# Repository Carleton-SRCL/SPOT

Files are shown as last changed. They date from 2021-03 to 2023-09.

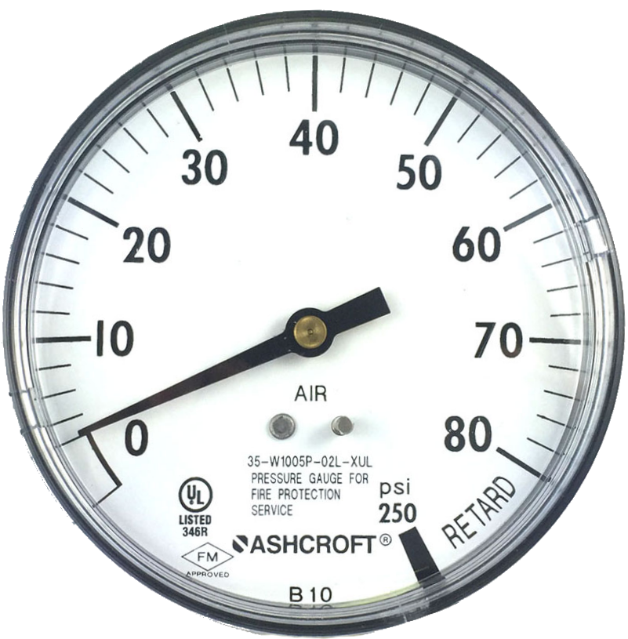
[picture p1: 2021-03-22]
CAD_Files/99 - Textures/guage.png

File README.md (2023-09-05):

# Welcome to SPOT

This testbed is used by researchers to investigate robotics, control and computer vision technologies enabling spacecraft proximity operation tasks, such as inspection maneuvers, rendezvous and docking, robotic capture of a tumbling target, and on-orbit assembly of large structure. SPOT consists of three air-bearing spacecraft platforms operating in close proximity on a granite surface. The use of air bearing on the platforms reduces the friction to a negligible level. Both platforms are actuated by compressed air expelled through small air nozzles, to provide three degree-of-freedom (3DOF) control authority. The motion of all platforms is measured in real-time through LEDs which are tracked by a motion capture system. This provides highly accurate ground truth position and attitude data to evaluate the performance of the new robotics, control, and computer vision technologies.

This repository contains the software developed for SPOT. The software is a mix of Simulink code (making use of existing code that allows us to deploy the Simulink diagrams to a NVIDIA Jetson Xaviers), and custom device driver blocks written in C++ code. It's been designed to be user-friendly, but is a constant work in progress so feedback and bug reports are appreciated. This repository also contains a detailed Wiki on the entire laboratory in an attempt to help guide new users. New users should read this Wiki carefully and watch any related videos before conducting an experiment.

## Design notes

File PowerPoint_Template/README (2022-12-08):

This is a repository to hold Microsoft PowerPoint (.pptx and .potx) template files specifically for use by SRCL students on related work.

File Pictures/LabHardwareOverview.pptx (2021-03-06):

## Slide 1

PhaseSpace Impulse X2E System
H/W: Intel Quad Core
Motion Tracking Camera Array
S/W: Custom Linux Software

Wireless Ethernet (UDP)

Off-Board Development Computer
H/W: Intel Core i7 5775 3.3 GHz
S/W: Window 10, MATLAB 9.8, Simulink 10.1
MATLAB/Simulink Support Package for Raspberry Pi 20.1.0

Wireless Ethernet (UDP)

Air Bearings

On-Board Control Computer
H/W: Raspberry Pi 3 Model B
S/W: Raspbian Linux (10)

Digital Outputs

Analog Outputs

On-Board Machine Learning Computer
H/W: NVIDIA Jetson TX2 Series
S/W: Linux Driver Package (L4T)

On-Board Control Computer
H/W: Raspberry Pi 3 Model B
S/W: Raspbian Linux (10)

Digital Outputs

Analog Outputs

Inertial Measurement Unit
H/W: Yost Labs 3-Space
S/W: Driver 1.1.7

Thrusters

Reaction Wheel

Thrusters

Air Bearings

Robotic Manipulator
H/W: Electromagnetic Dock

Reaction Wheel

Inertial Measurement Unit
H/W: Yost Labs 3-Space
S/W: Driver 1.1.7

Target Spacecraft

Serial (RS232)

On-board Vision System
H/W: ZED 2 Stereo Camera
S/W: OpenCL

Ethernet Hub

Robotic Manipulator
H/W: Dynamixel MX-64
Custom Gripper

Chaser Spacecraft

Serial (RS232)

Granite Table
(3.5 m by 2.4 m)

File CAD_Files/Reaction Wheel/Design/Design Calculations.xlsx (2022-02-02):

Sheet: Mass
Mass Budget

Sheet: Dim
 | POP SSS Sizing |  | 2017-02-05
 | gcs2kgms | gcc2kgcm | mu (km^3/s^2) | Re (km) | g (m/s^2) | R_geo (km) | w_geo (rad/s) | psi2Pa
 | 1e-07 | 1000 | 398600.4418 | 6378.136 | 9.81 | 42164.173 | 7.292115082e-05 | 6894.75789
 | rpm2rps | lbf2N | kg2lb | ft2in | in2cm | deg2rad | rad2deg
 | 0.105 | 4.448222 | 2.20462 | 12 | 2.54 | 0.017 | 57.3
Dimension Scale | 10 | 0.1 | Mass Scale | 200 | 0.005 | Time Scale | 10 | 0.1
Platform Mass Margin |  | 4 |  |  |  | Mission Time Margin |  | 2.25
Bus Sizing | Actual | Platform |  | Actual | Platform | Time Rel Qnty | Actual | Platform
CS bus Dimension |  |  | CS bus mass |  |  | Time (s) | 10 | 1
x length (cm) | 236.2 | 23.6 | BOL Mass (kg) | 3085.5 | 15.4 | Min Linear
y length (cm) | 222.7 | 22.3 | MOL Mass (kg) | 2289 | 11.4 | Min Velocity (m/s) | 0.0145 | 0.0145
z length (cm) | 312.4 | 31.2 | EOL Mass (kg) | 1651.8 | 8.3 | Min Accel (m/s^2) | 0.0135 | 0.135
Solar Panel |  |  | Moment Arm |  |  | Min Angular
CS solar panel (single) |  |  | Expressed in RCSCS |  |  | Min Ang Vel (deg/s) | 0.064 | 0.064
x length (cm) | 212.0 | 21.2 | x COM (cm) | 0.0 | 0.0 | Min Ang Accl (deg/s^2) | 0.000322 | 0.0322
y length (cm) | 312.4 | 31.2 | y COM (cm) | 0.0 | 0.0 | Min Ang Vel (rad/s) | 0.001123992038 | 0.001123992038
z length (cm) | 1.0 | 0.1 | z COM (cm) | 107.8 | 10.8 | Req Ang Vel (rad/s) | 0.001118962667 | 0.01118962667
CS solar panel (total) |  |  |  |  |  | Req Error (rad/s) | 5.029370827e-06 | -0.01006563464
x length (cm) | 212.0 | 21.2 |  |  |  | Min Ang Accl (rad/s^2) | 5.619960191e-06 | 0.0005619960191
y length (cm) | 1329.4 | 132.9 | MOI |  |  | Max Linear
z length (cm) | 1.0 | 0.1 | Expressed in RCSBS |  |  | Max Velocity (m/s) | 0.0135 | 0.0135
num panels | 4.3 |  | xx MOI (kgm^2) | 7123.4 | 0.356 | Max Accel (m/s^2) | 0.0145 | 0.145
 |  |  | yy MOI (kgm^2) | 71.4 | 0.004 | Max Angular
 |  |  | zz MOI (kgm^2) | 7205.6 | 0.360 | Req Ang Vel (rad/s) | 3 | 3
 |  |  | xy MOI (kgm^2) | -1.2 | -6e-05 | Req Error (rad/s) | 0.0 | 0.0
 |  |  | xz MOI (kgm^2) | 0.0 | 0.000 | Max Ang Vel (deg/s) | 3.0 | 3.0
 |  |  | yz MOI (kgm^2) | 0.0 | 0.000 | Max Ang Accl (deg/s^2) | 0.015 | 1.5
 |  |  |  |  |  | Max Ang Vel (rad/s) | 0.05 | 0.05
 |  |  |  |  |  | Max Ang Accl (rad/s^2) | 0.0002617993878 | 0.02617993878
Table Space | (m) | (cm) | Platform MOI Requirement | Unit | Platform | Mission Duration | Actual | Platform
x length | 241.3 | 241.3 | CS yy MOI | (kgm^2) | 0.80 | sec | 33750 | 3375
z length | 350.52 | 350.5 | Margin |  | 2 | min | 562.5 | 56.25
precision | (micro in) | 23.6 | CS yy MOI Req | (kgm^2) | 0.40 | hr | 9.375 | 0.9
 | (micron) | 0.6 | SS yy MOI | (kgm^2) | 0.96 | mission phase
 |  |  | Margin |  | 2 | Phase 1 (min) | 50 | 5
 |  |  | SS yy MOI | (kgm^2) | 0.48 | Phase 2 (min) | 50 | 5
 |  |  |  |  |  | Phase 3 (min) | 50 | 5
 |  |  | Example LEO Orbit | Unit | Actual | Phase 4 (min) | 100 | 10
 |  |  | Altitude | (km) | 450 | Phase 5 (min) | 50 | 5
 |  |  | Orbit Radius | (km) | 6828.13649
 |  |  | Orbit Freq | (rad/s) | 0.001118962667
 |  |  |  | (rpm) | 0.011
 |  |  | Orbit Period | (min) | 93.58646018
Thruster Sizing | Unit | Platform | Wheel Sizing | Unit | Platform | Impulse Requirement | Actual | Platform
Inlet Pressure | (psi) | 20 | Wheel Diameter | (in) | 4 | Pulse Time (s) | 1 | 0.1
Diameter | (mm) | 4 | Height | (in) | 2 | Minimum Impulse Bit
Efficiency |  | 0.5 | Wheel Diameter | (cm) | 10.2 | Num Thruster | 2 | 2
 | (in) | 0.16 | Wheel Height | (cm) | 5.1 | Force per Thruster (lbf) | 2.5 | 0.1
Pressure | (lbf) | 0.2 | Shaft 1 Tolerance |  | 0.1 | After Efficiency Force (N) | 22.2993 | 1.114965
 | (N) | 0.9 | Shaft 1 Diameter | (inch) | 0.95 | After Efficiency Force (lbf) | 5.013081631 | 0.3
Exit Area | (in^2) | 0.02 |  | (cm) | 2.4 | Force per Thruster (N) | 11.14965 | 0.5574825
Num Thruster in Dir |  | 2 | Shaft 1 Length | (inch) | 1.5 | Impulse Bit (Ns) | 22.2993 | 0.1
Total Thrust in Dir | (N) | 1.732841659 |  | (cm) | 3.9 | Delta-V (mm/s) | 13.5 | 13.5
Thruster Pulses |  |  | Shaft 2 Diameter ratio |  | 3 | Maximum Impulse Bit
Minimum |  |  | Shaft 2 Diameter | (inch) | 0.5 | After Efficiency Force (N) | 44.73975 | 2.2369875
Thrust Duration | (sec) | 0.1 |  | (cm) | 1.2 | After Efficiency Force (lbf) | 10.05789504 | 0.5028947521
Impulse Bit | (Ns) | 0.2 | Shaft 2 Length | (inch) | 0.5 | Num Thruster | 4 | 2
Maximum |  |  |  | (cm) | 1.2 | Force per Thruster (lbf) | 2.5 | 0.3
Thrust Duration | (sec) | 1.0 | Wheel Area | (cm^2) | 81.07319666 | Force per Thruster (N) | 11.1849375 | 1.11849375
Impulse Bit | (Ns) | 1.7 | Shaft 1 Area | (cm^2) | 4.599605804 | Impulse Bit (Ns) | 44.73975 | 0.2
 |  |  | Shaft 2 Area | (cm^2) | 1.130973355 | Delta-V (mm/s) | 14.5 | 14.5
MW Motor Sizing | Unit | Platform | Wheel Volume | (cm^3) | 411.851839 | Timings
Gear Box Ratio Calculation |  |  | Shaft 1 Volume | (cm^3) | 17.93846264 | Reaction Timing (s) | 20 | 2
Input Motor Rate | (rpm) | 6800 | Shaft 2 Voume | (cm^3) | 1.334548559 | Minimum Impulse Bit
 | (rad/s) | 712.0943348 | Total Wheel Volume | (cm^3) | 392.5788278 | Req Veh Pitch Torque (Nm) | 0.0004815181892 | 0.0005417079629
Output Ang Rate | (rad/s) | 13.43574217 | Wheel Material |  | Stainless Steel | Req Veh Pitch Torque (mNm) | 0.482 | 0.542
 | (deg/s) | 769.8113208 | Wheel Density | (g/cm^3) | 7.955 | Ang Impulse Bit (Nms) | 0.009630363784 | 0.001
Input Torque | (mNm) | 1.61 | % Volume |  | 1 | Vehicle angular acc (rad/s^2) | 0.0001123992038 | 0.001123992038
Output Torque | (mNm) | 25.23484299 | Wheel Mass | (kg) | 3.1 | Vehicle angular acc (deg/s^2) | 0.00644 | 0.0644
Margin |  | 2 |  | (lb) | 6.884950162 | Vehicle velocity (rad/s) | 0.001 | 0.001
Output With Margin | (mNm) | 50.46968598 | Wheel Area Section 1 | (cm^2) | 76.47359085 | Vehicle velocity (deg/s) | 0.064 | 0.064
GB Ratio |  | 53 | Wheel Area Section 2 | (cm^2) | 79.9422233 | Stack angular rate (rad/s) | 1.590560529e-08 | 0.0001655095759
Est. GB Efficiency |  | 0.59 | Wheel Volume Section 1 | (cm^3) | 298.2470043 | Stack angular rate (deg/s) | 9.113240536e-07 | 0.01
Final Motor GB Combination |  |  | Wheel Volume Section 2 | (cm^3) | 94.33182349 | Stack angular rate (rpm) | 1.518873423e-07 | 0.001580500028
Motor+GB Combined Length | (cm) | 5.34 | Mass Section 1 | (kg) | 2.4 | Stach rotation period (min) | 6583827.099 | 632.7
Motor+GB Inertia | (kgm^2) | 1.43e-06 | Mass Section 2 | (kg) | 0.8 | Maximum Impulse Bit
Load Inertia | (kgm^2) | 0.0074 | Wheel Inertia Section 1 | (kgm^2) | 0.0032 | Req Veh Pitch Torque (Nm) | 0.022 | 0.025
Load Inertia/Rotor Inertia Ratio |  | 5157.308392 | Wheel Inertia Section 2 | (kgm^2) | 0.0010 | Req Veh Pitch Torque (mNm) | 22.4 | 25.2
Gear Ratio req. base on Inertia |  | 71.8144024 | Wheel Inertia CORRECTED BY KIRK | (kgm^2) | 0.0074 | Ang Impulse Bit (Nms) | 0.4486194309 | 0.050
Check GB Ratio | (req.>95%) | 0.74 | Spin Rate | (rpm) | 128.3018868 | Vehicle angular acc (rad/s^2) | 0.005 | 0.052
Motor+GB Out Stall Torque | (mNm) | 248.2839844 | Allowed Spin Rate | (rpm) | 128.3018868 | Vehicle angular acc (deg/s^2) | 0.3 | 3
Motor+GB Out Nominal Torque | (mNm) | 149.428828 | delta |  | 0 | Vehicle velocity (rad/s) | 0.052 | 0.052
Output Speed | (rpm) | 128.3018868 |  | (rev/s) | 2.1 | Vehicle velocity (deg/s) | 3.0 | 3.0
Mechanical Time Constant | (s) | 414.2121638 |  | (rad/s) | 13.43574217 | Stack angular rate (rad/s) | 7.409443457e-07 | 0.007710073412
Motor |  |  |  | (deg/s) | 769.8113208 | Stack angular rate (deg/s) | 4.245298386e-05 | 0.44
Reference | Maxon | http://www.maxonmotor.com/medias/sys_master/root/8816806527006/15-257-EN.pdf | Kinetic Energy | (J) | 0.7 | Stack angular rate (rpm) | 7.075497311e-06 | 0.07362577771
Serial | 339260 | Maxon-EC32flat-32mm,brushless,6W,with Hall | Angular Mom | (Nms) | 0.10 | Stach rotation period (min) | 141332.8217 | 13.6
Mass | (kg) | 0.032 | Margin |  | 2.0 | RWA Design Check | Unit | Platform
Kt | (mNm/A) | 13.2 |  |  |  | Desired platform RPM | rpm | 10
Motor Efficiency |  | 0.57 | Stack Dynamics | Actual | Platform | Desired platform Angular Rate | deg/s | 60
MOI | (gcm^2) | 13.9 | CS yy-MOI Percent Increase | 1.0 | 225 |  | rad/s | 1.047197551
 | (kgm^2) | 1.39e-06 | CS yy-MOI (kgm^2) | 71.4 | 0.80 | Required Wheel Angular Momentum | Nms | 1.00939372
Diameter | (cm) | 3.2 | SS yy-MOI Percent Increase | 1.2 | 270 | Required Wheel MOI Multiplication |  | 10.18684734
Length | (cm) | 1.8 | SS yy-MOI (kgm^2) | 85.68 | 0.96 | Max Platform Angular Rate | deg/s | 5.89
Shaft Diameter | (cm) | 0.4 | Stack CG-CG Distance (cm) | 312.4 | 31.2 | Seconds Per Full Rotation | s | 61.12
Shaft Length | (cm) | 1.0 | MOI addition from CS (kgm^2) | 30116.41041 | 1.5 | Rotations Per Minute | rpm | 0.98
Time Constant | (ms) | 80.3 | Stack yy-MOI (kgm^2) | 30273.49041 | 3.3 | Minutes Per Rotation | min | 1.02
Voltage | (V) | 12 | Initial Condition
Max Power | (W) | 6 | CS Initial Ang Vel (rad/s) | 0.001118962667 | 0.01118962667 | RWA Design Check | Unit | Platform
Max Current | (A) | 0.50 | CS Initial Ang Vel (deg/s) | 0.06 | 0.64 | Required Min Torq on Platform | (Nm) | 0.0005417079629
Idle speed | (rpm) | 7970 | CS Initial Rot Period (min) | 93.58646018 | 9.36 | Required Max Torq on Platform | (Nm) | 0.025
Max Motor Torque | (mNm) | 7.98 | CS Ang Mom (kg-m^2/s) | 0.08 | 0.009 | Max Torq by Gearbox Output | (Nm) | 0.149
Check Max Torque Margin |  | 4.94 | SS Initial Ang Vel (rad/s) | 0.001118962667 | 0.01118962667 | Required Max Ang Mom | (Nms) | 0.050
Running Speed | (rpm) | 6800 | SS Ang Mom (kg-m^2/s) | 0.10 | 0.011 | Max Stack Ang Mom | (Nms) | 0.050
 | (rad/s) | 712.0943348 | Total Ang Mom (kg-m^2/s) | 0.18 | 0.02 | Max Ang Mom Store in Wheel | (Nms) | 0.099
Running Torque | (mNm) | 4.80 | Post stack |  |  | Max Input Torque | (mNm) | 1.61
Check Running Torque Margin |  | 2.98 | % increase Dlt-H FFC (kg-m^2/s) | 1.55 | 1.55 | Max Motor Torque Capable | (mNm) | 7.98
Gear Box |  |  | Total Ang Post FFC (Nms) | 0.45 | 0.05 | Max Computed Motor rate | (rpm) | 6800
Reference | Maxon | http://www.maxonmotor.com/medias/sys_master/root/8816808460318/15-295-296-EN.pdf | Post FFC Ang Vel (rad/s) | 1.480519643e-05 | 0.01540590087 | Max GB input speed | (rpm) | 8000
Serial | 143980 | Planetary Gearhead GP22C | Post FFC Ang Vel (deg/s) | 0.001 | 0.883 | Require Gear Ratio |  | 53.0
Gear Ratio |  | 53 | Post FFC Rot Period (min) | 7073.175664 | 6.797379525 | Selected Gear Ratio |  | 52.7
Absolute Reduction |  | 52.734375
Shaft Diameter | (cm) | 0.4 | Manipulator Sizing | Unit | Platform | Manipulator Design | Unit | Platform
 | (inch) | 0.157 | Link Selection |  |  | Joints
Shaft Length | (cm) | 1.17 | Material |  | carbon fiber | Number of joints |  | 3
Diameter | (cm) | 2.2 | Type |  | Tube | Joint types |  | SR,SY,SP,EP,WP,WY,WR
 | (inch) | 0.866 | Density | (g/cm^3) | 1.55 | Number of links |  | 2
Length | (cm) | 3.9 |  | (kg/m^3) | 1550 | Link types |  | SB,WB
 | (inch) | 1.535 | Bending Tensile Strength | (ksi) | 300 | Power
Mass | (kg) | 0.068 |  | (MPa) | 2068.427367 | Maximum Power | (W) | 72.72
 | (lb) | 0.150 | Bending Modulus | (Msi) | 15 | Power Ref | SRCL-SSFP-150601-01-SK-Mission_Phase_Power_Budget-R1.xls
MOI | (gcm^2) | 0.4 |  | (GPa) | 103.4213683 | Bus Voltage | (V) | 12
 | (kgm^2) | 4e-08 | Bending Shear Modulus | (Msi) | 0.6 | WR | (W) | 24.24
Max Axial Load | (N) | 100 |  | (GPa) | 4.1 | WY | (W) | 24.24
Max Force for Press Fits | (N) | 100 | Torsion Tensile Strength | (ksi) | 20 | WP | (W) | 24.24
Number of Stages |  | 3 |  | (MPa) | 137.8951578 | EP | (W) | 24.24
Avg Backlash No Load | (deg) | 1.6 | Torsion Modulus | (Msi) | 2.2 | SP | (W) | 24.24
GB Efficiency |  | 0.59 |  | (GPa) | 15.16846736 | SY | (W) | 24.24
Max Input Speed | (rpm) | 8000 | Torsion Shear Modulus | (Msi) | 4.5 | SR | (W) | 24.24
 |  |  |  | (GPa) | 31.0264105 | WR Running Current | (A) | 2.02
Max Continuous Torque | (mNm) | 1200 | Boom |  |  | WY Running Current | (A) | 2.02
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

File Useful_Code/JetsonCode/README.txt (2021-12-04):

jetsonRepeater.py is run on the Jetson and communicates to: 1) the Pi; 2) any other scripts running on the Jetson
use_deep_guidance_arm.py is an example of another script that is run on the Jetson and interfaces with the Pi via the jetsonRepeater.py
The remaining scripts are used to capture or perform CNN-inference with the Zed camera.

For a Simulink example of communicating with the Pi, see: https://github.com/Kirkados/SPOT/tree/main/Projects/Kirk_Phase3 and look at the Kirk_Phase3.slx diagram

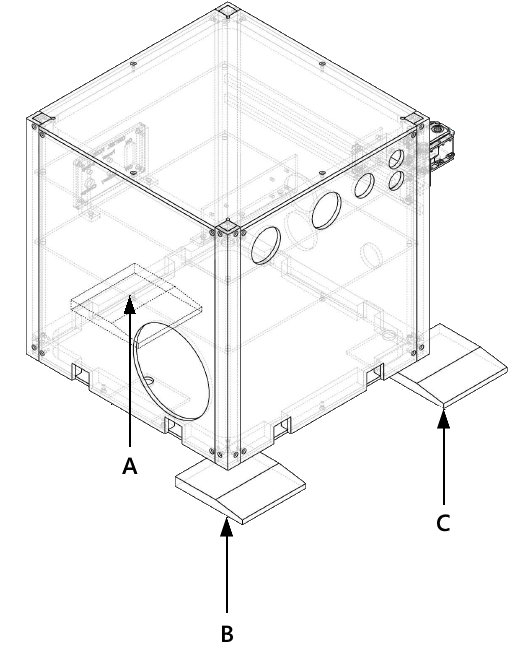
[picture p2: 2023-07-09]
Projects/Capstone_2023_2024/Resources/config_for_com.png

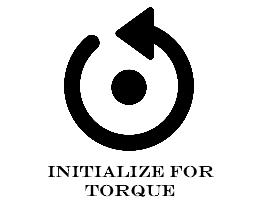
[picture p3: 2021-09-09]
Custom_Library/InitTorque.png

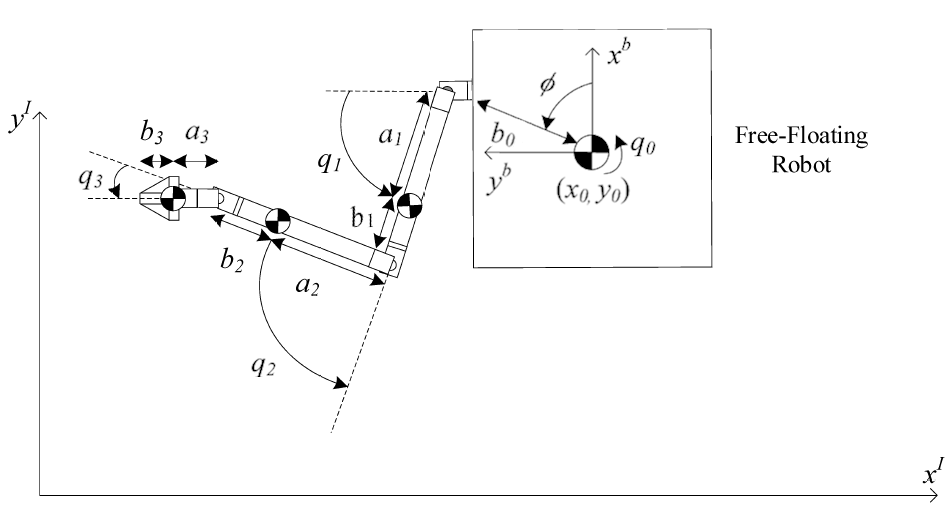
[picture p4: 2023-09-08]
Projects/Capstone_2023_2024/Resources/ArmConfig.png

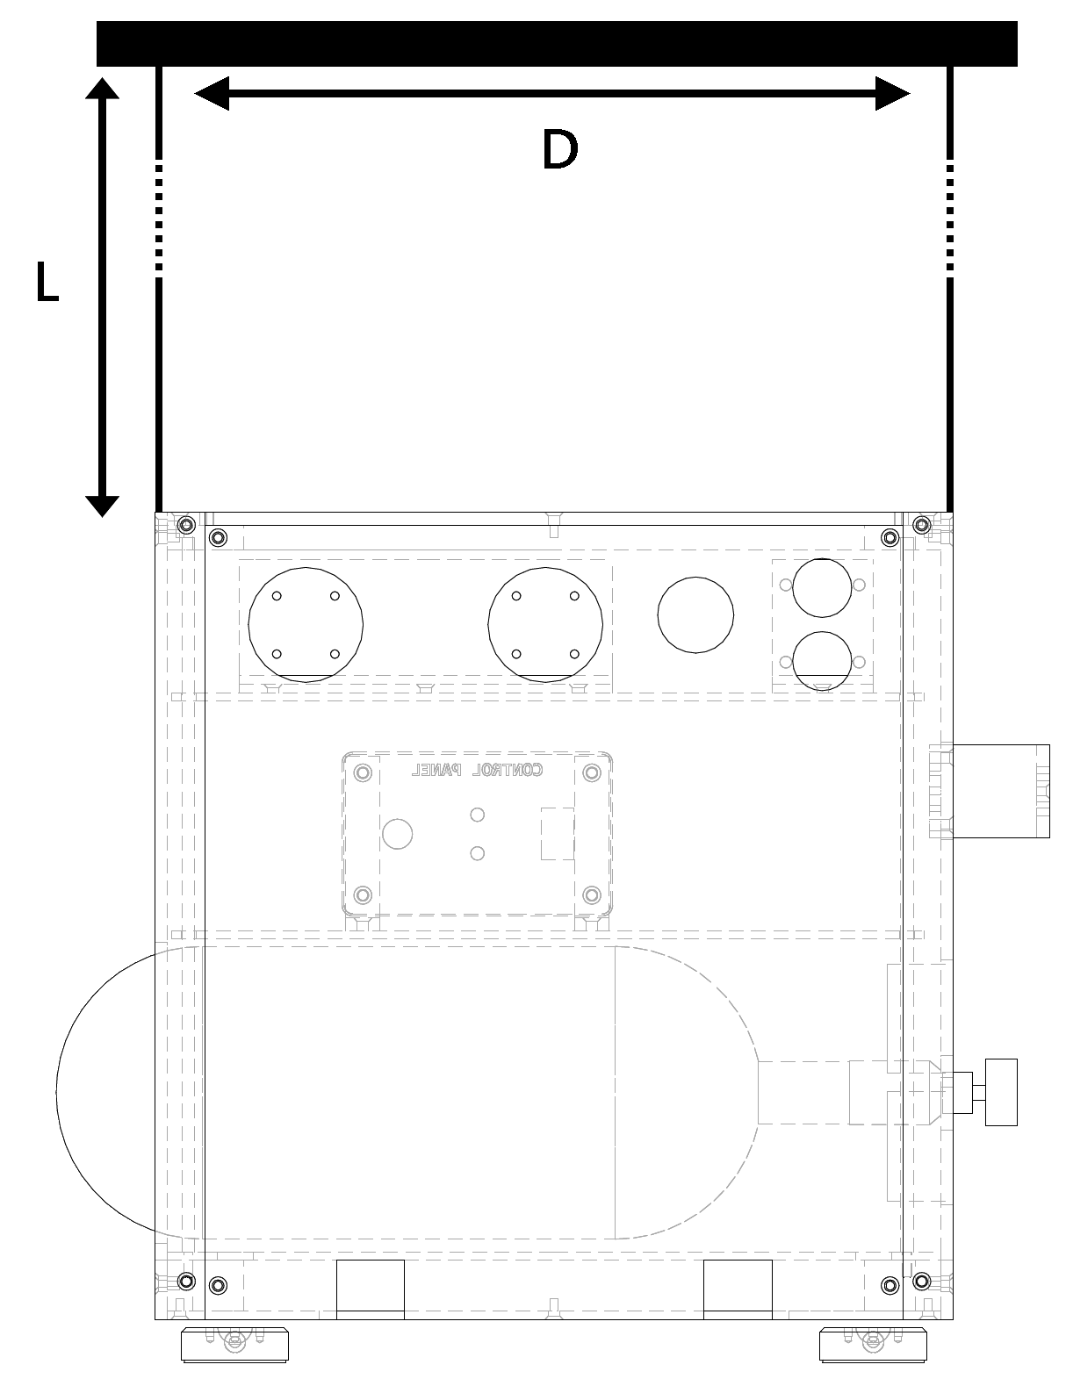
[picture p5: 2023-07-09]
Projects/Capstone_2023_2024/Resources/config_for_inertia.png

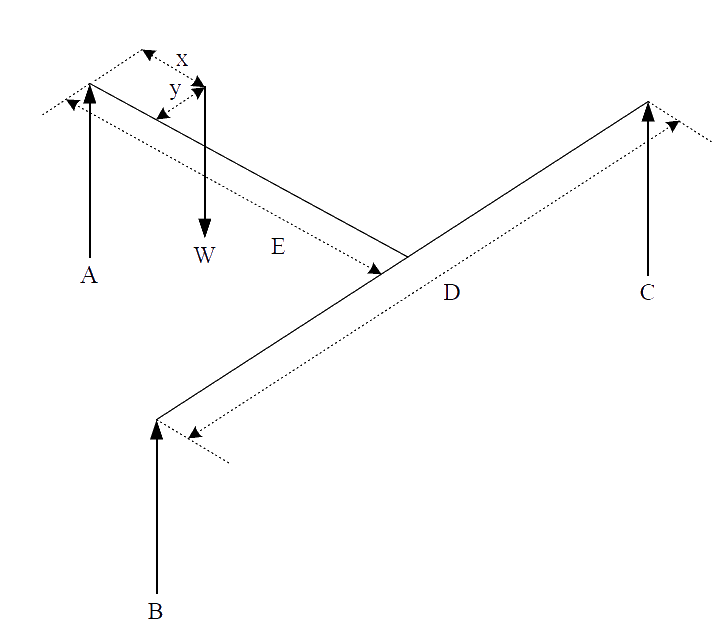
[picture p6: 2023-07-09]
Projects/Capstone_2023_2024/Resources/fbd_for_com.png

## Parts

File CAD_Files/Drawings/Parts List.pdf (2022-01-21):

PART NUMBER | DESCRIPTION | QTY | NOTES
SSFP-001 | Corner Bracket | 8 | QTY of 4 will be used in SSFP-018. Apply
| | | surface finish where applicable
SSFP-002 | Top | 2
SSFP-003 | Rod | 8
SSFP-004 | Bus Deck | 2
SSFP-005 | Protective Plate | 2
SSFP-006 | Deck(AV+SENS) | 4
SSFP-007 | Arm Bracket | 2 | QTY of 2 will be used in SSFP-018. Apply
| | | surface finish where applicable
SSFP-008 | Arm Coupler | 2
SSFP-009 | Control Panel Bracket | 4
SSFP-010 | LIDAR Mount | 2
SSFP-011 | Stereo Mount | 2
SSFP-012 | Control Panel | 2 | Will discuss means of applying text
SSFP-013 | Back Panel | 2
SSFP-014 | Front Panel | 2
SSFP-015 | Left Panel | 2
SSFP-016 | Right Panel | 2
SSFP-017 | Top Panel | 2
SSFP-018 | Weld ASSY | 2

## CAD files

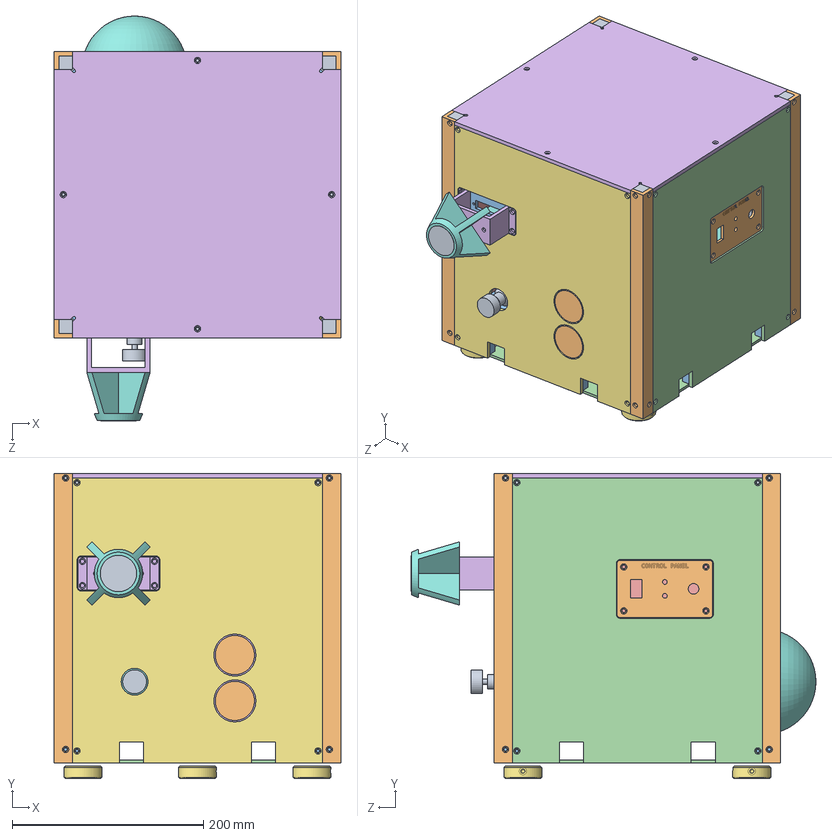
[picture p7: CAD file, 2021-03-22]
CAD_Files/00 - Full_Lab_Assemblies/servicer_no-arm_dock_stereo-ZED.SLDASM
300.0 x 319.3 x 424.0 mm
top
corner-bracket x 4
arm_bracket
panel_back
panel_front
deck_avionics
control_panel_bracket x 2
control_panel
deck_sensor
camera_VIS-mount
camera_Lidar-mount
panel_right
puck x 3
air_tank
air_tank_valve
pressure-gauge x 2
deck_bus
protective_plate
rod x 4
arm_coupler
stereo_camera_ZED-Body
male_cone
disk

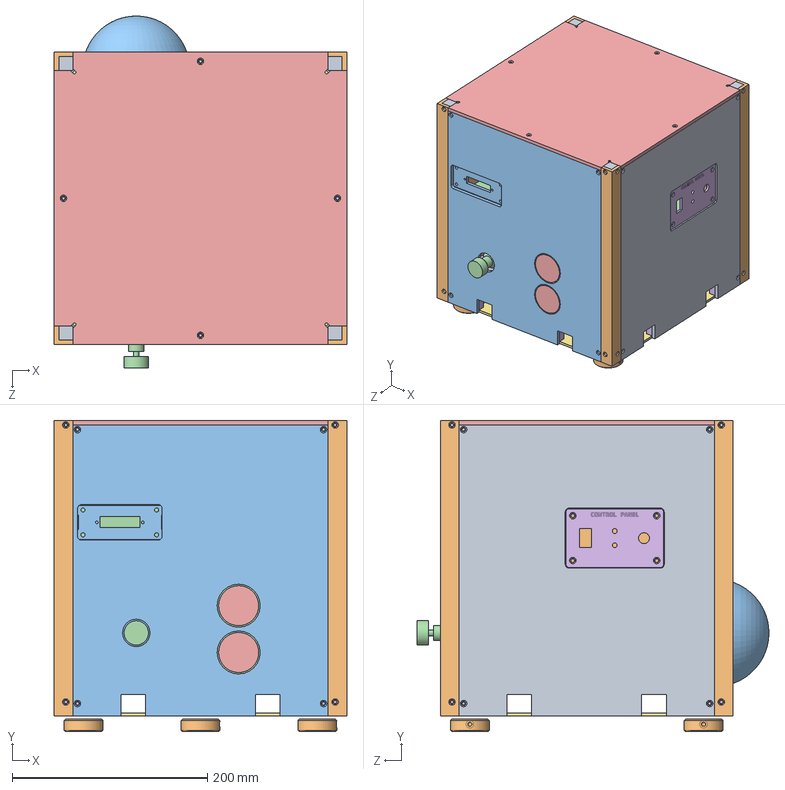
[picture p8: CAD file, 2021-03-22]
CAD_Files/01 - Target/FULLASSY_client.SLDASM
300.0 x 319.4 x 361.0 mm
top
corner-bracket x 4
arm_bracket
deck_avionics
control_panel_bracket x 2
control_panel
deck_sensor
camera_VIS-mount
camera_Lidar-mount
puck x 3
air_tank
air_tank_valve
pressure-gauge x 2
deck_bus
protective_plate
rod x 4
panel_back_black
panel_front_black
panel_left_black
panel_right_black
panel_top_black

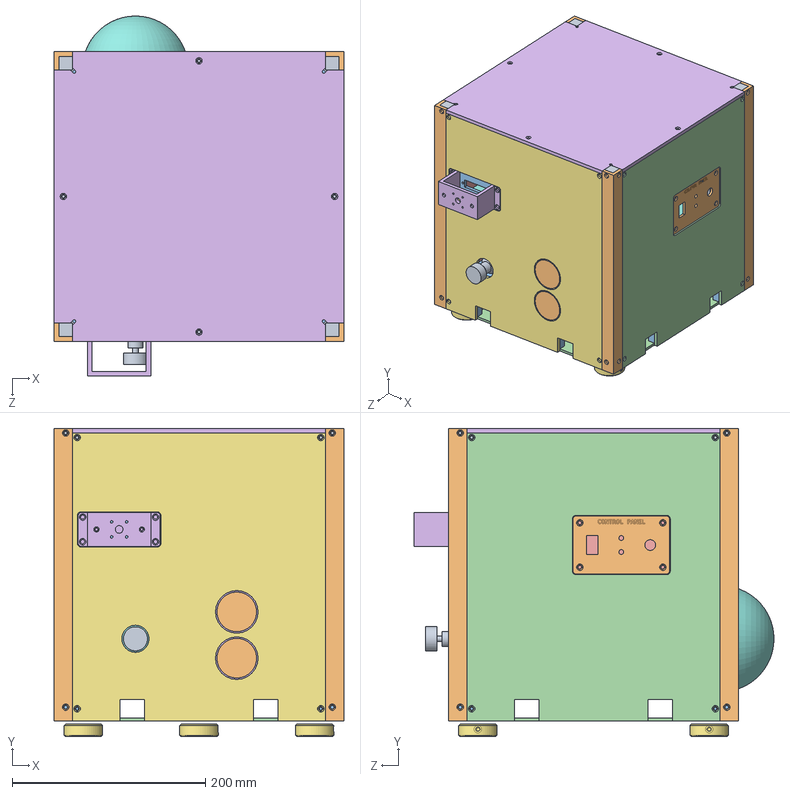
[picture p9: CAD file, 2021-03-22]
CAD_Files/02 - Chaser/FULLASSY_servicer.SLDASM
300.0 x 319.3 x 373.0 mm
top
corner-bracket x 4
arm_bracket
panel_back
panel_front
panel_top
panel_left
deck_avionics
control_panel_bracket x 2
control_panel
deck_sensor
camera_VIS-mount
camera_Lidar-mount
panel_right
puck x 3
air_tank
air_tank_valve
pressure-gauge x 2
deck_bus
protective_plate
rod x 4
arm_coupler

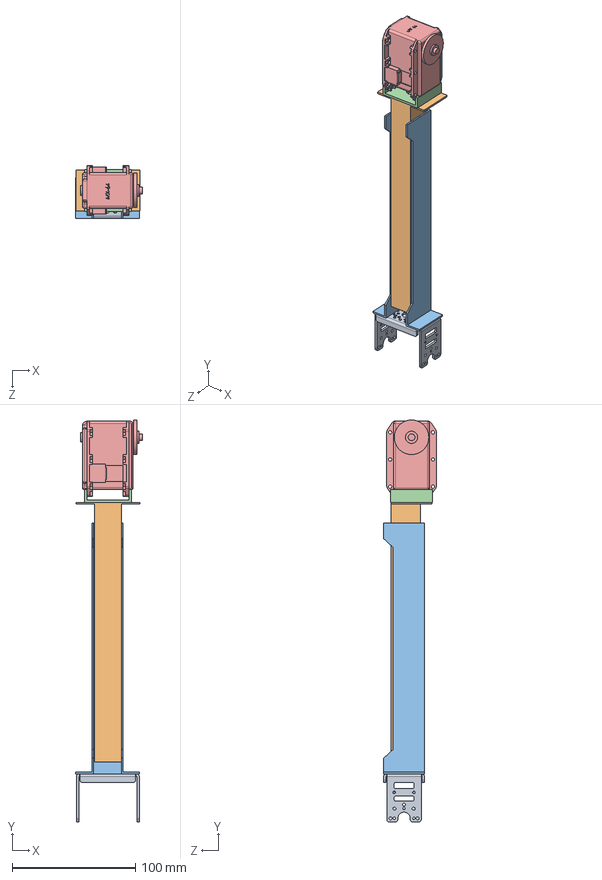
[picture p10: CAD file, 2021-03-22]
CAD_Files/03 - Arm/arm_link_ASSY.SLDASM
54.1 x 325.7 x 42.7 mm
FR05-H101
Inner Girder
Outer Girder
RX-64 BRKT
MX-64T

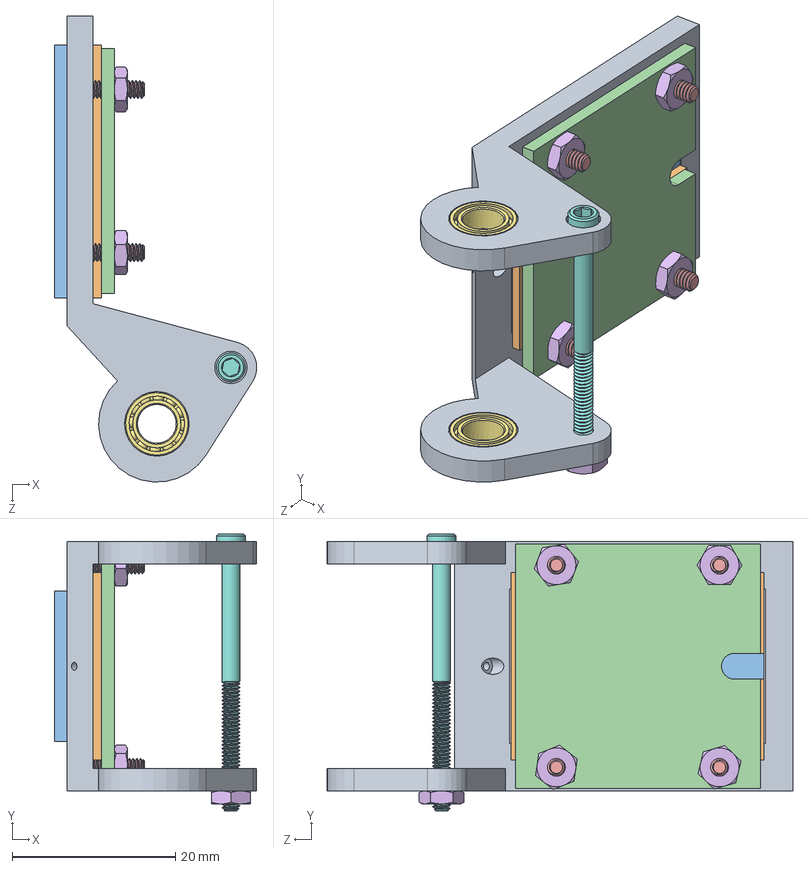
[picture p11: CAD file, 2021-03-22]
CAD_Files/04 - Gripper/distal_R_ASSY.SLDASM
24.8 x 33.9 x 57.1 mm
distal_R
contactpad_base
contactpad_rubber
contactpad_plate
2-56_flatscrew_91253A079 x 4
2-56_nut_90480A003 x 5
ball-bearing_57155K352 x 2
2-56_socketscrew_91251A195

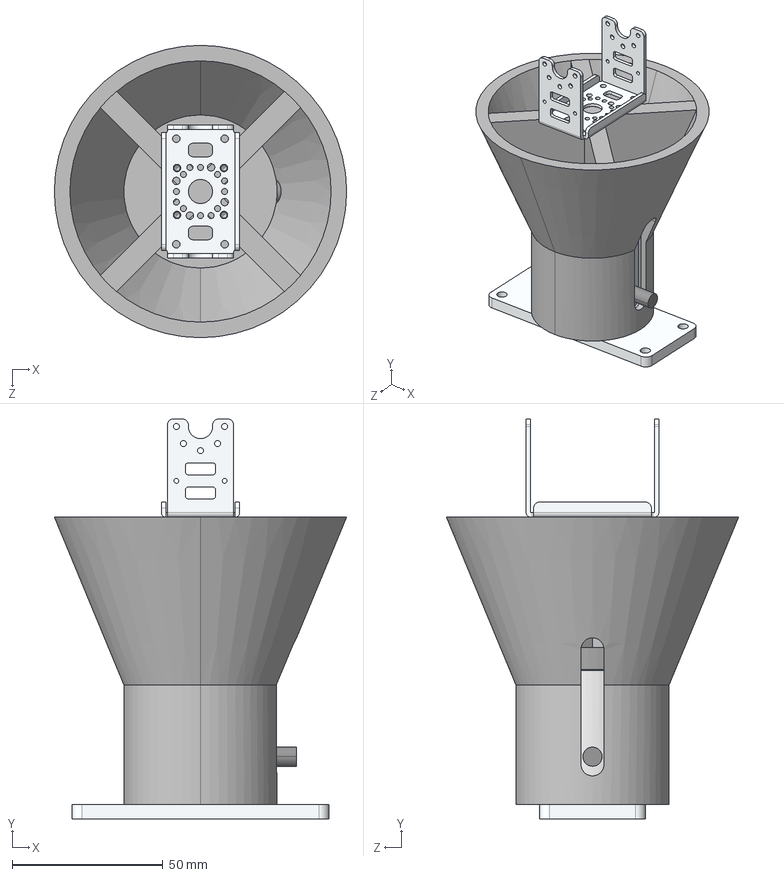
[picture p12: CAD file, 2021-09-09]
CAD_Files/07 - Magnetic_Dock/ASSY_MALE-FEMALE.STEP
96.8 x 132.5 x 96.8 mm
5698K115_SURFACE-CONTACT DC-POWERED ELECTROMAGNET_5698K115
female_cone
interface_bracket
male_cone
disk
FR07-H101_arm-bracket-large

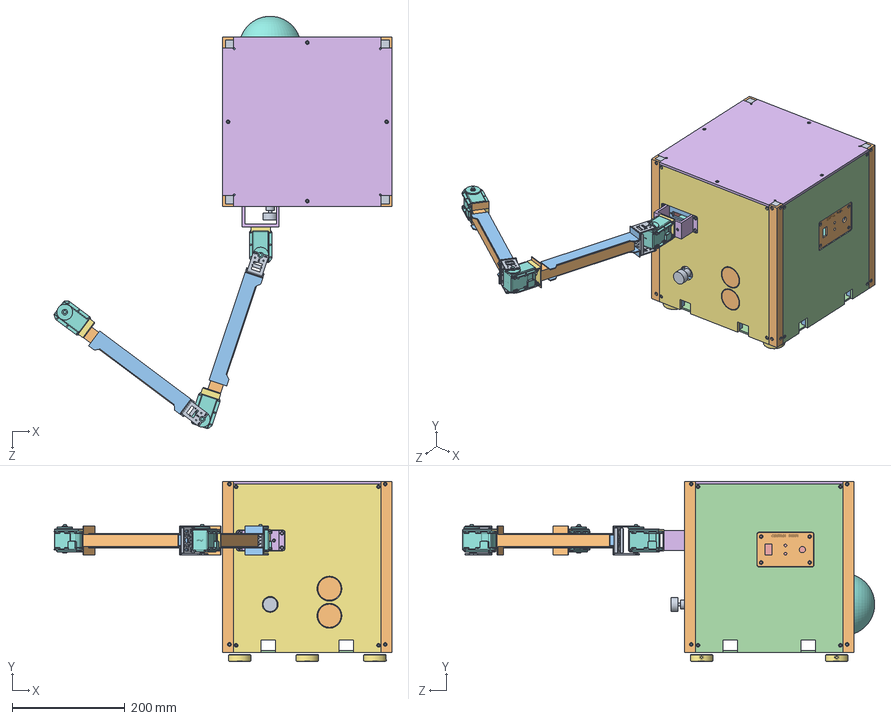
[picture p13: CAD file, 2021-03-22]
CAD_Files/00 - Full_Lab_Assemblies/servicer_arm_nogripper.SLDASM
598.9 x 319.3 x 730.8 mm
top
corner-bracket x 4
arm_bracket
panel_back
panel_front
panel_top
panel_left
deck_avionics
control_panel_bracket x 2
control_panel
deck_sensor
camera_VIS-mount
camera_Lidar-mount
panel_right
puck x 3
air_tank
air_tank_valve
pressure-gauge x 2
deck_bus
protective_plate
rod x 4
arm_coupler
RX-64 BRKT x 3
MX-64T x 3
FR05-H101 x 2
Inner Girder x 2
Outer Girder x 2

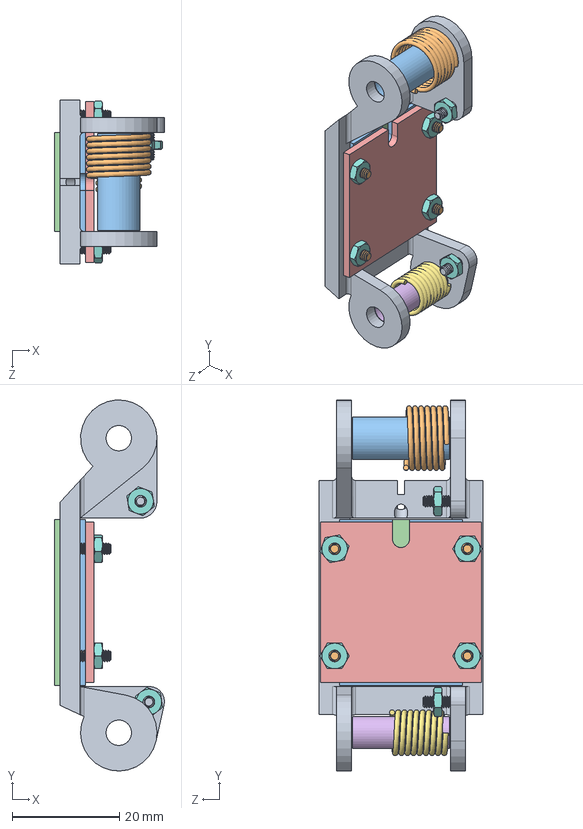
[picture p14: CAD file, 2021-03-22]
CAD_Files/04 - Gripper/proximal_R_ASSY.SLDASM
20.5 x 69.3 x 30.6 mm
proximal_R
2-56_flatscrew_91253A079 x 4
contactpad_base
contactpad_rubber
contactpad_plate
spacer_long_proximal
spring_prox_LHW
2-56_nut_90480A003 x 6
2-56_flatscrew_91253A078 x 2
spring_dist_RHW
spacer_long_distal

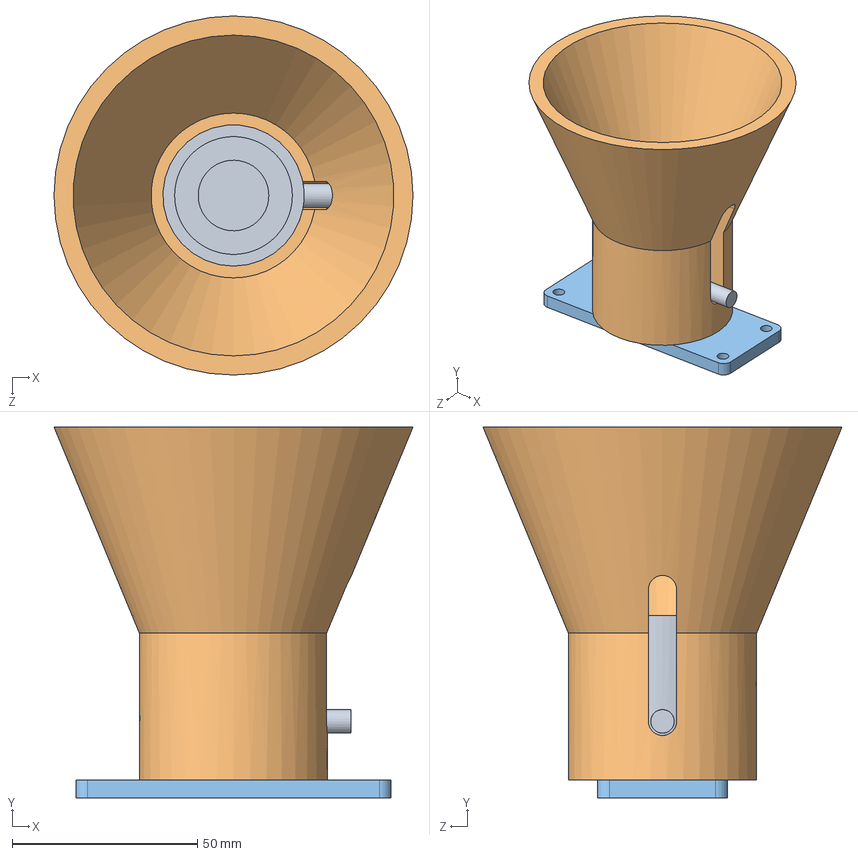
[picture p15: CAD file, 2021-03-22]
CAD_Files/07 - Magnetic_Dock/ASSY_target.SLDASM
96.8 x 100.0 x 96.8 mm
5698K115_SURFACE-CONTACT DC-POWERED ELECTROMAGNET
female_cone
interface_bracket

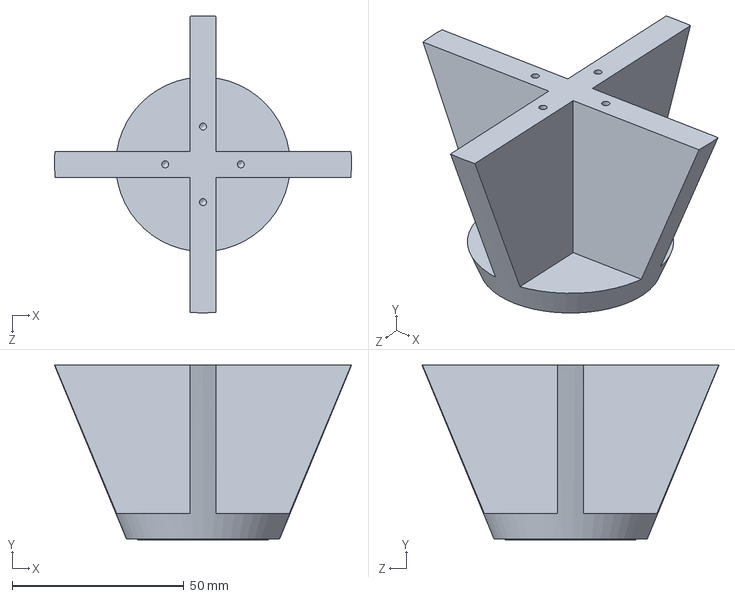
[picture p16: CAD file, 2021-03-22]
CAD_Files/07 - Magnetic_Dock/ASSY_male-cone.SLDASM
86.5 x 50.8 x 86.5 mm
male_cone
disk

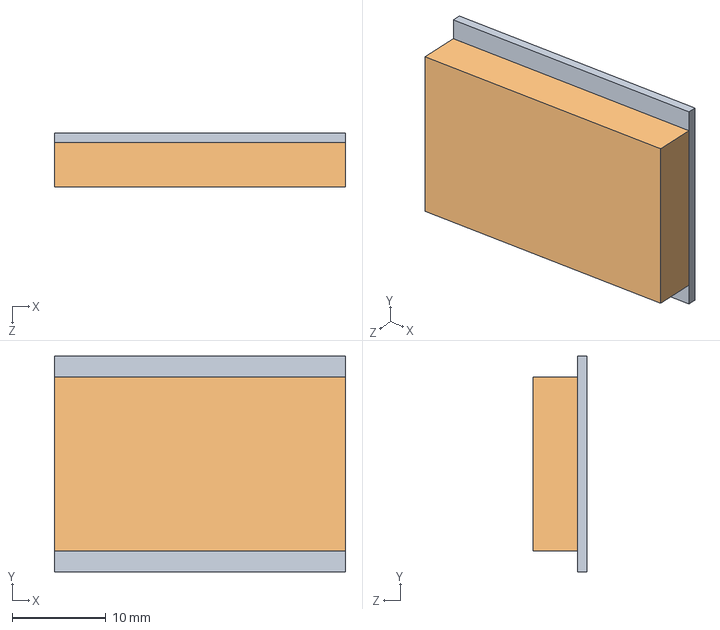
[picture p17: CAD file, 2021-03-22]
CAD_Files/04 - Gripper/contactpad_ASSY.SLDASM
31.0 x 23.0 x 5.78 mm
contactpad_base
contactpad_rubber

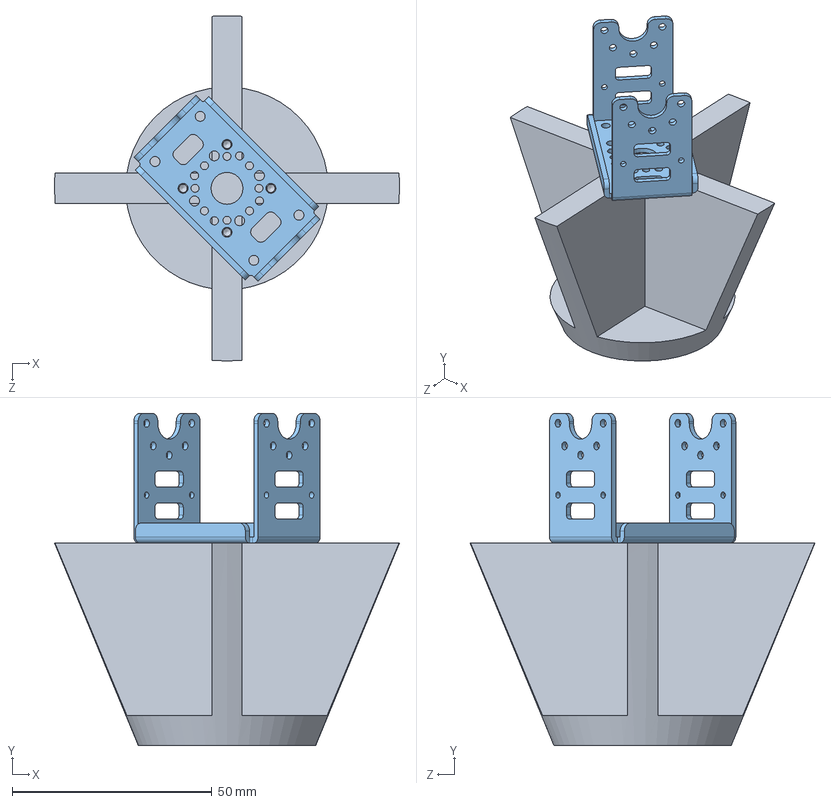
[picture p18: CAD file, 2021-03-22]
CAD_Files/07 - Magnetic_Dock/ASSY_servicer.SLDASM
86.5 x 83.3 x 86.5 mm
male_cone
disk
FR07-H101_arm-bracket-large

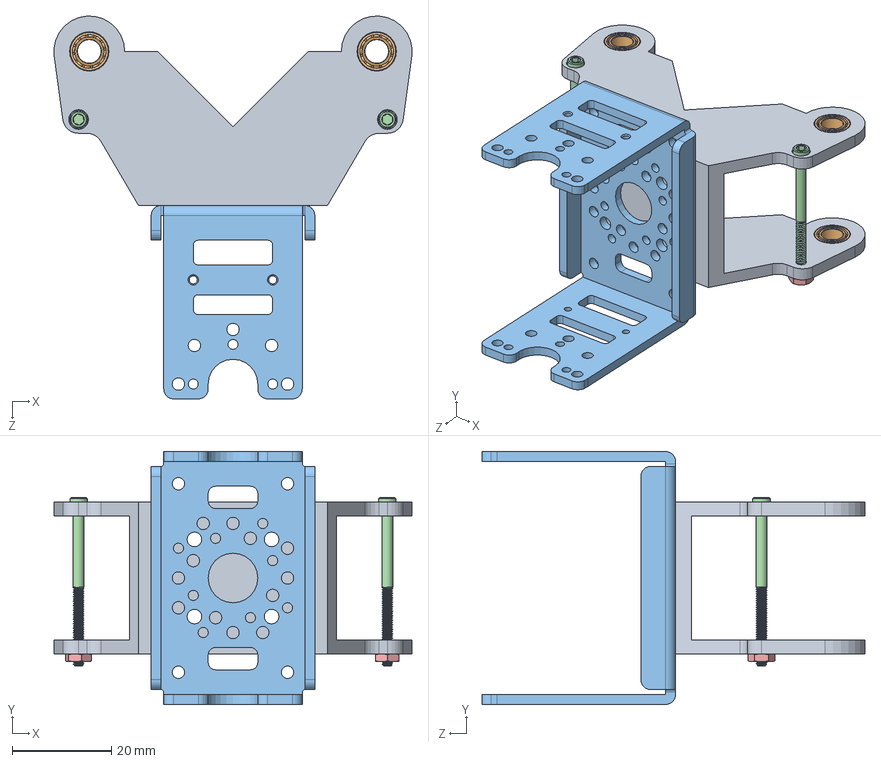
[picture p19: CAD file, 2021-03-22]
CAD_Files/04 - Gripper/gripper_base_ASSY.SLDASM
72.2 x 51.0 x 77.2 mm
gripper_base
ball-bearing_57155K352 x 4
actuator_bracket
2-56_socketscrew_91251A195 x 2
2-56_nut_90480A003 x 2

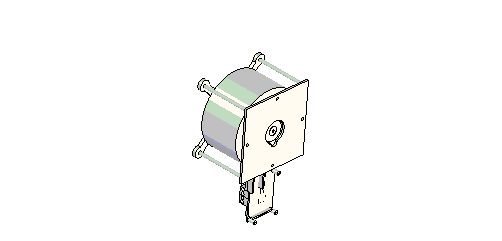
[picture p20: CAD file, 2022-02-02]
CAD_Files/Reaction Wheel/Solid Models/RWA1.sldasm
rwia_top_bracket1
rwia_adapter1
rwia_bottom_plate1
Maxon Gearbox1
rwia_top_plate1
rwia_top_tube1
Maxon Motor1
rwai_bbearing_ball1 x 11
rwia_bbearing_case1 x 2
rwa_wheel1
rwiea_pwr_cntr_fmle1 x 2
rwiea_connector_board1
stand_off1 x 3
rwiea_ctrl_chip1
rwiea_transistor1
rwiea_adaptor_board1

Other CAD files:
CAD_Files/Reaction Wheel/Solid Models/bbearing.SLDASM
CAD_Files/04 - Gripper/proximal_L_ASSY.SLDASM
CAD_Files/Reaction Wheel/Solid Models/rwia.SLDASM
CAD_Files/Reaction Wheel/Solid Models/rwiea.SLDASM
CAD_Files/03 - Arm/FR05-H101.sldprt
CAD_Files/03 - Arm/Inner Girder.sldprt
CAD_Files/03 - Arm/MX-64T.sldprt
CAD_Files/03 - Arm/Outer Girder.sldprt
CAD_Files/03 - Arm/RX-64 BRKT.sldprt
CAD_Files/04 - Gripper/2-56_flatscrew_91253A078.SLDPRT
CAD_Files/04 - Gripper/2-56_flatscrew_91253A079.SLDPRT
CAD_Files/04 - Gripper/2-56_nut_90480A003.SLDPRT
CAD_Files/04 - Gripper/2-56_socketscrew_91251A079.SLDPRT
CAD_Files/04 - Gripper/2-56_socketscrew_91251A195.SLDPRT
CAD_Files/04 - Gripper/8-32_nut_90480A009.SLDPRT
CAD_Files/04 - Gripper/actuator_bracket.SLDPRT
CAD_Files/04 - Gripper/ball-bearing_57155K352.SLDPRT
CAD_Files/04 - Gripper/constraint_sizing.SLDDRW
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

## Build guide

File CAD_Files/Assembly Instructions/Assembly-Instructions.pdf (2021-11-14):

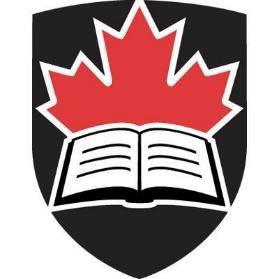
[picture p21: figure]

# S.P.O.T. ASSEMBLY MANUAL

SERVICER/CLIENT STRUCTURE

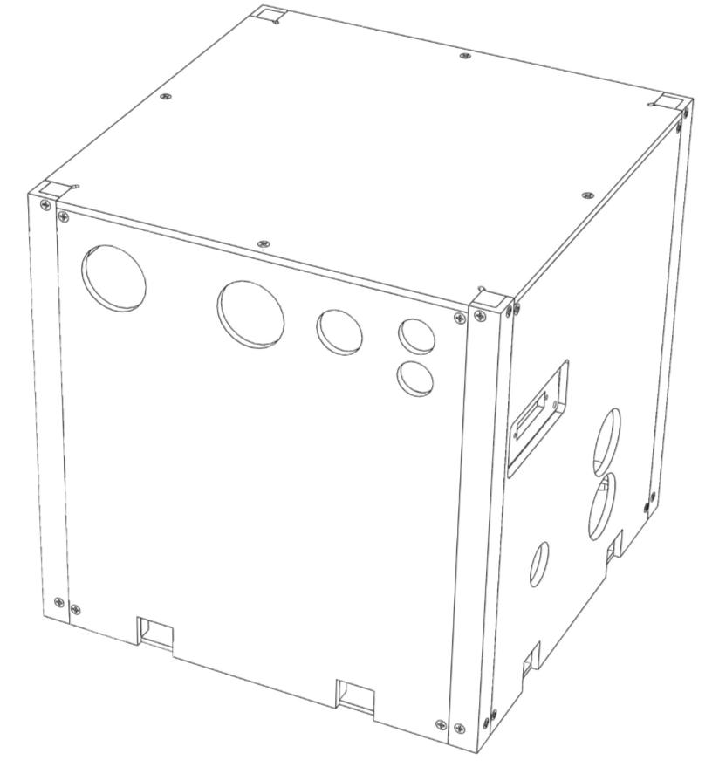
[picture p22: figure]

JULY 25, 2016

CARLETON UNIVERSITY SRCL

Justin Kernot

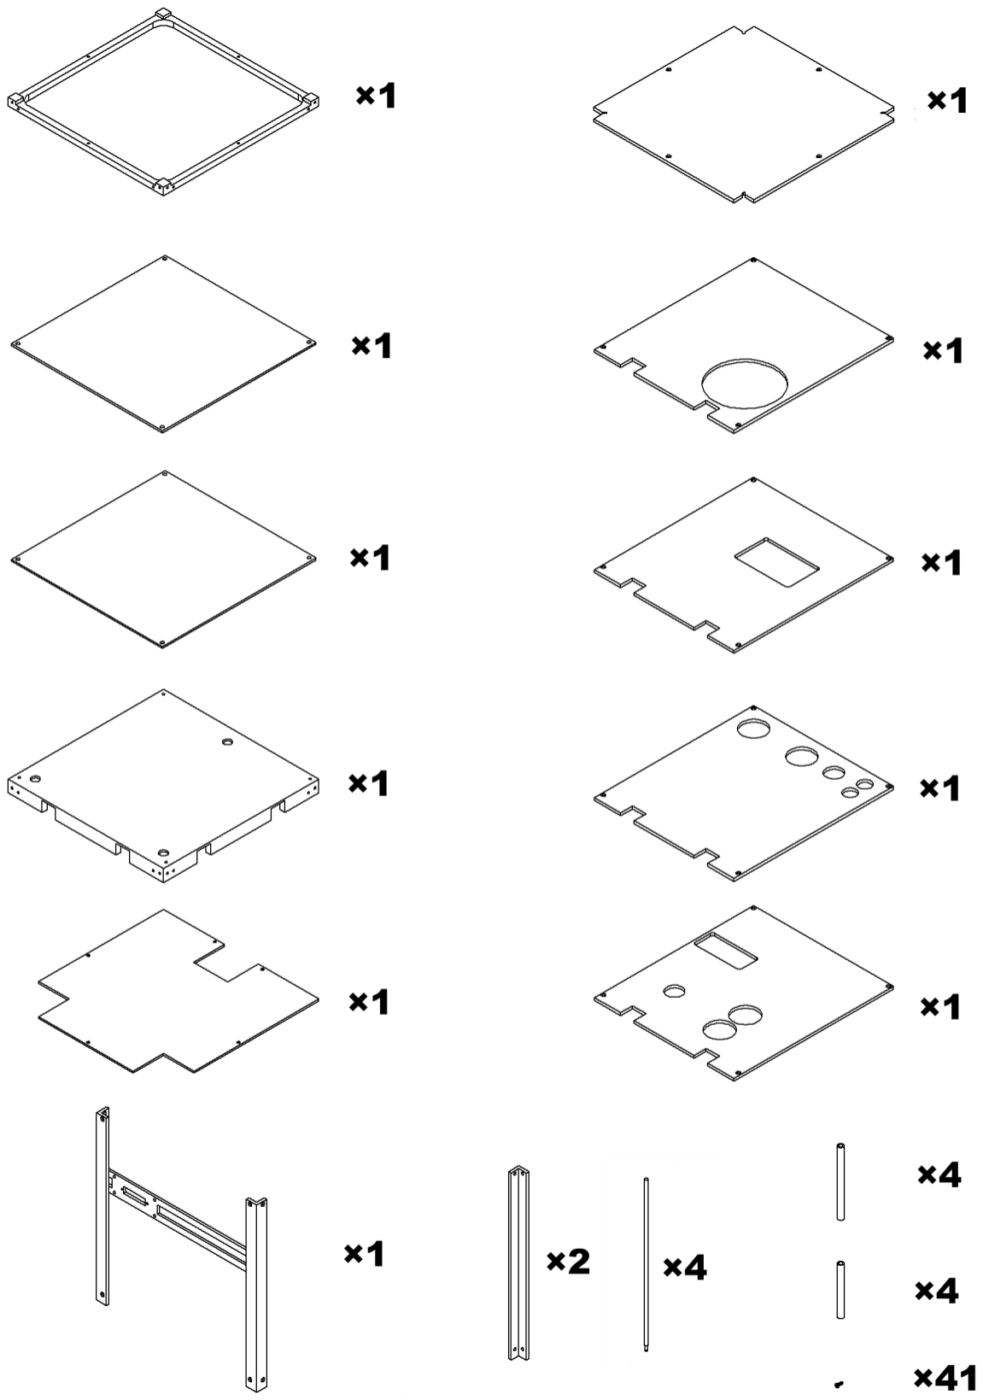
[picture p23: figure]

Page 1 of 9

## PARTS

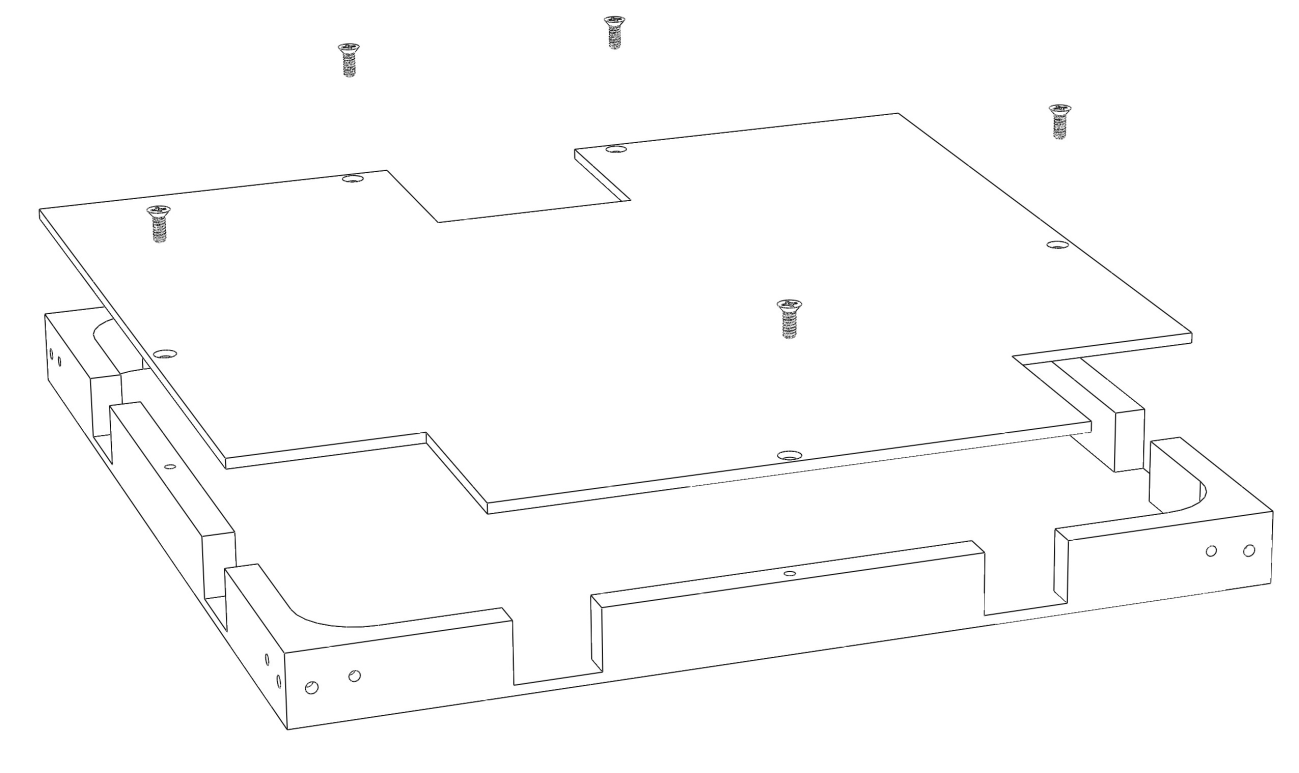
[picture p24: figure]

Page 2 of 9

## STEP 1

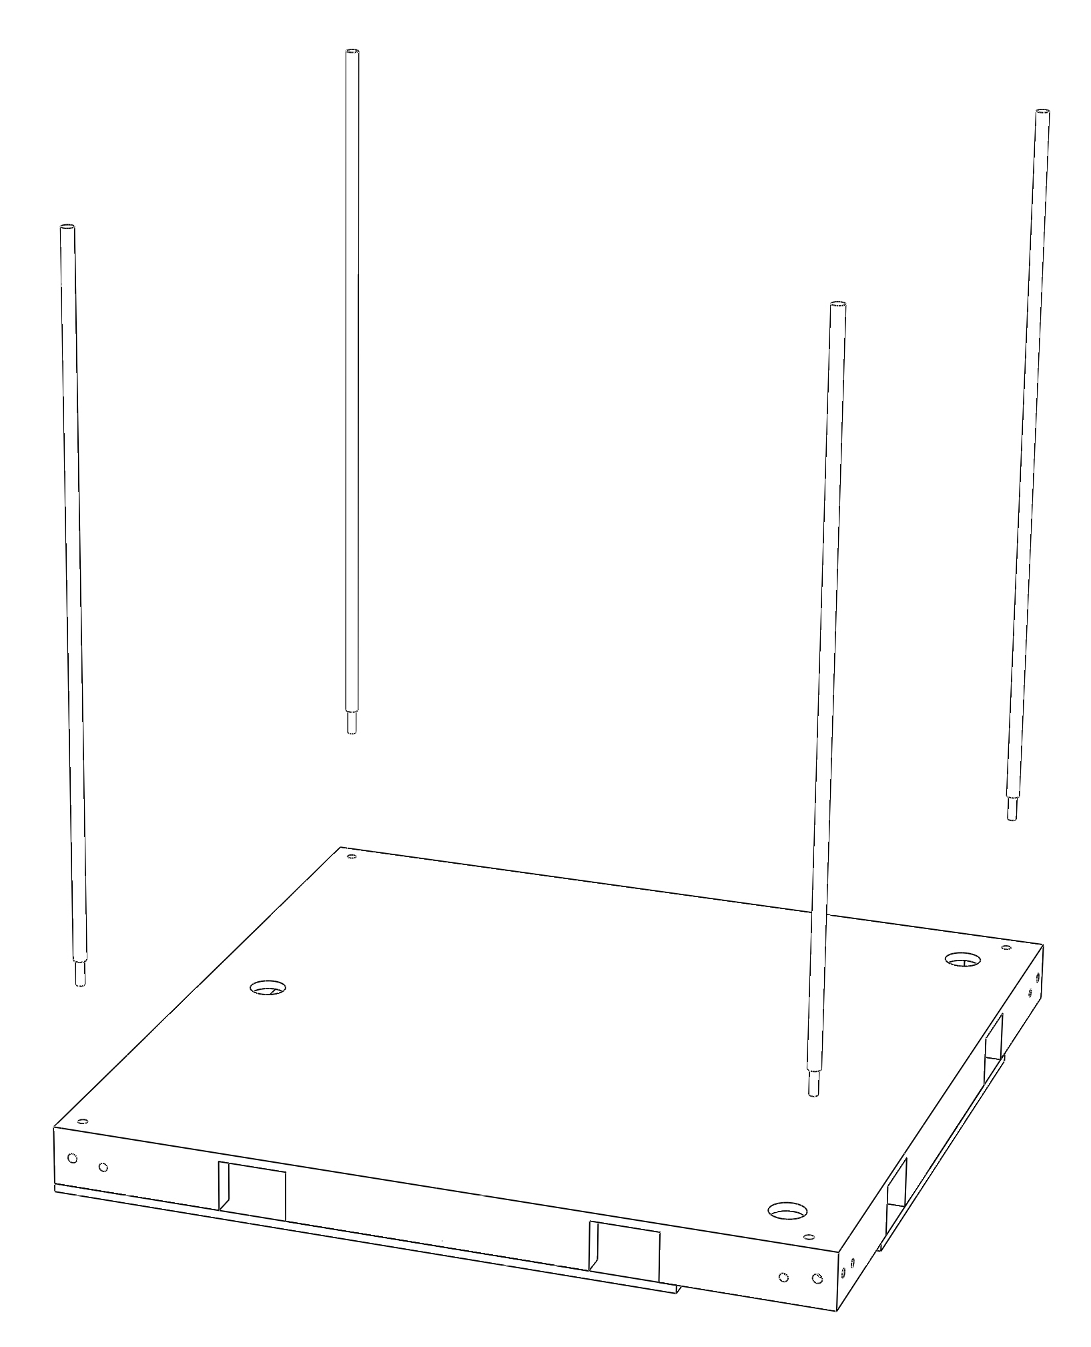
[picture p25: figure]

Page 3 of 9

## STEP 2

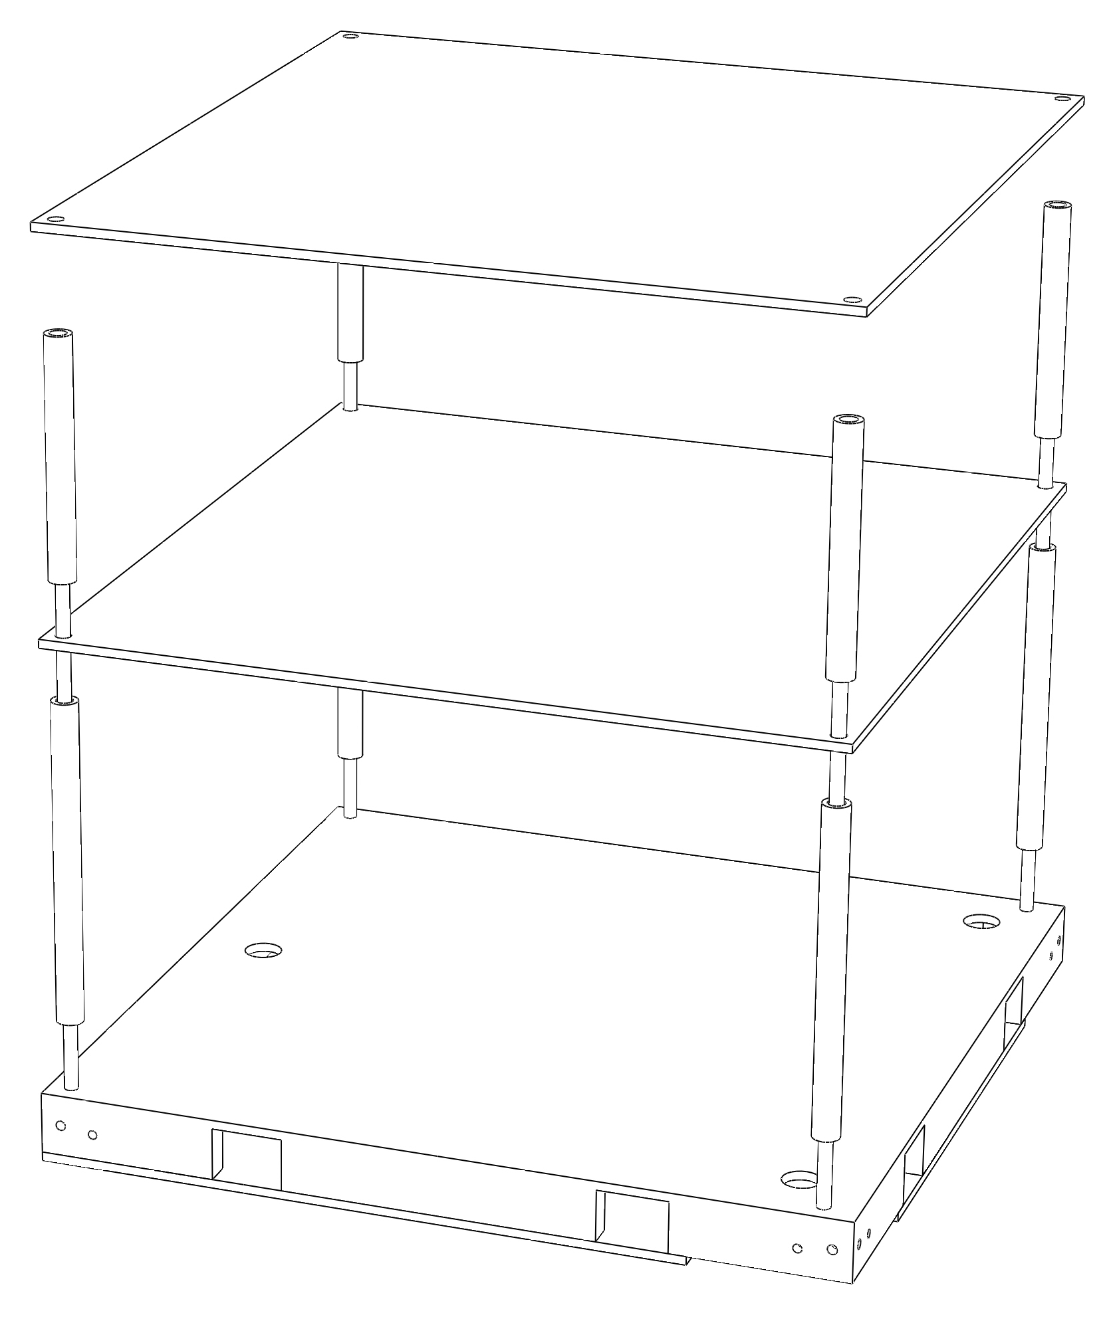
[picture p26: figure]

Page 4 of 9

## STEP 3

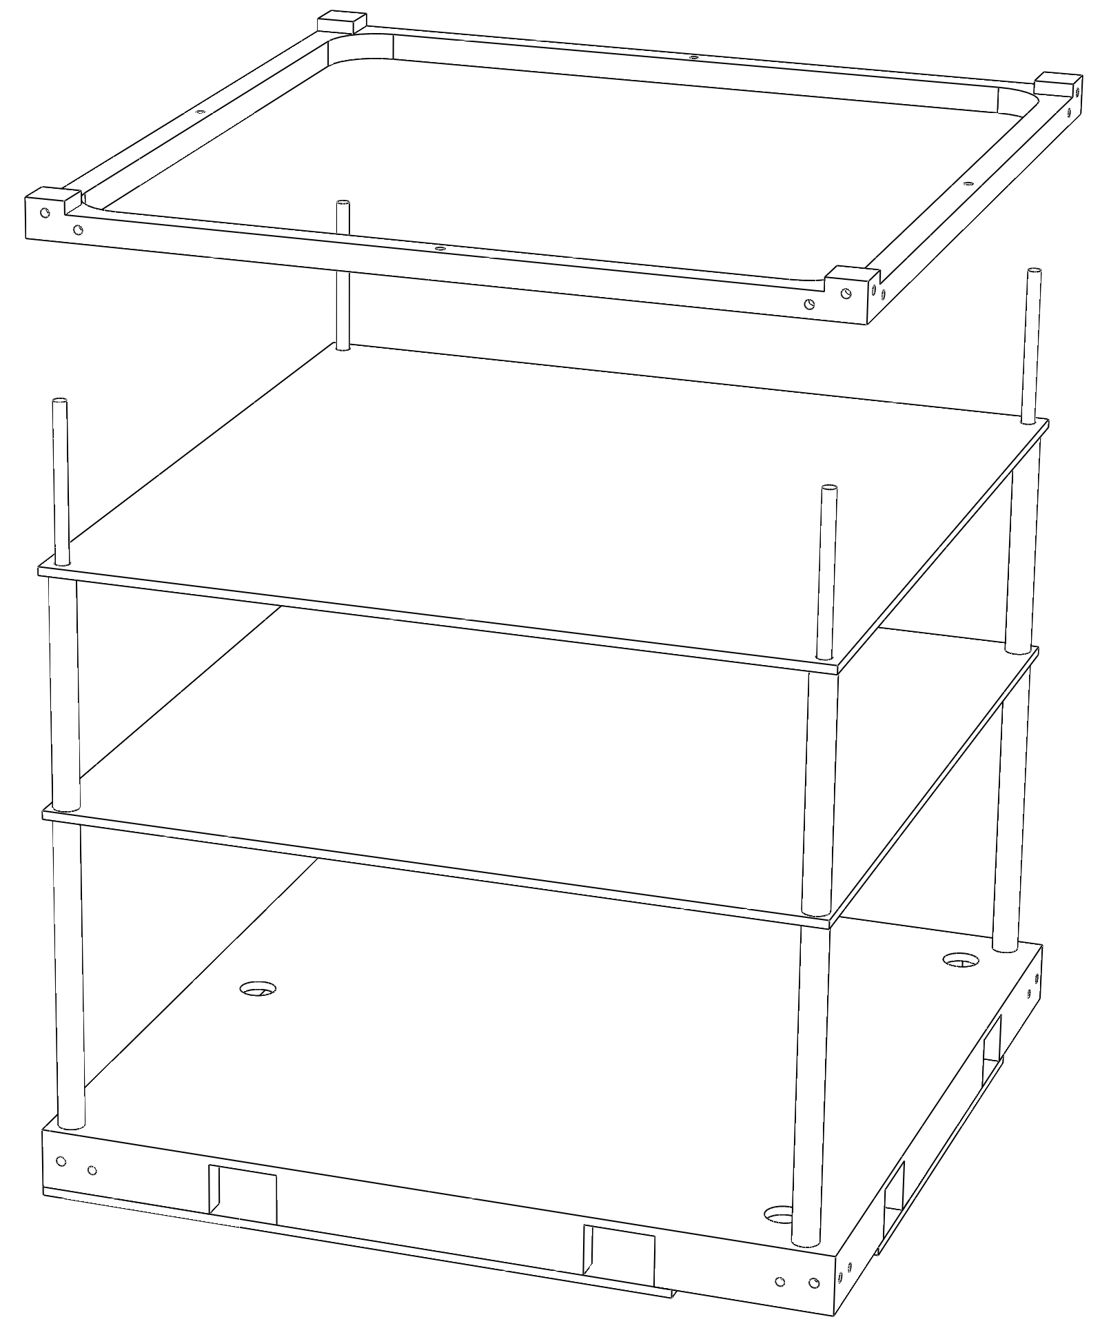
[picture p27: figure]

Page 5 of 9

## STEP 4

## STEP 5

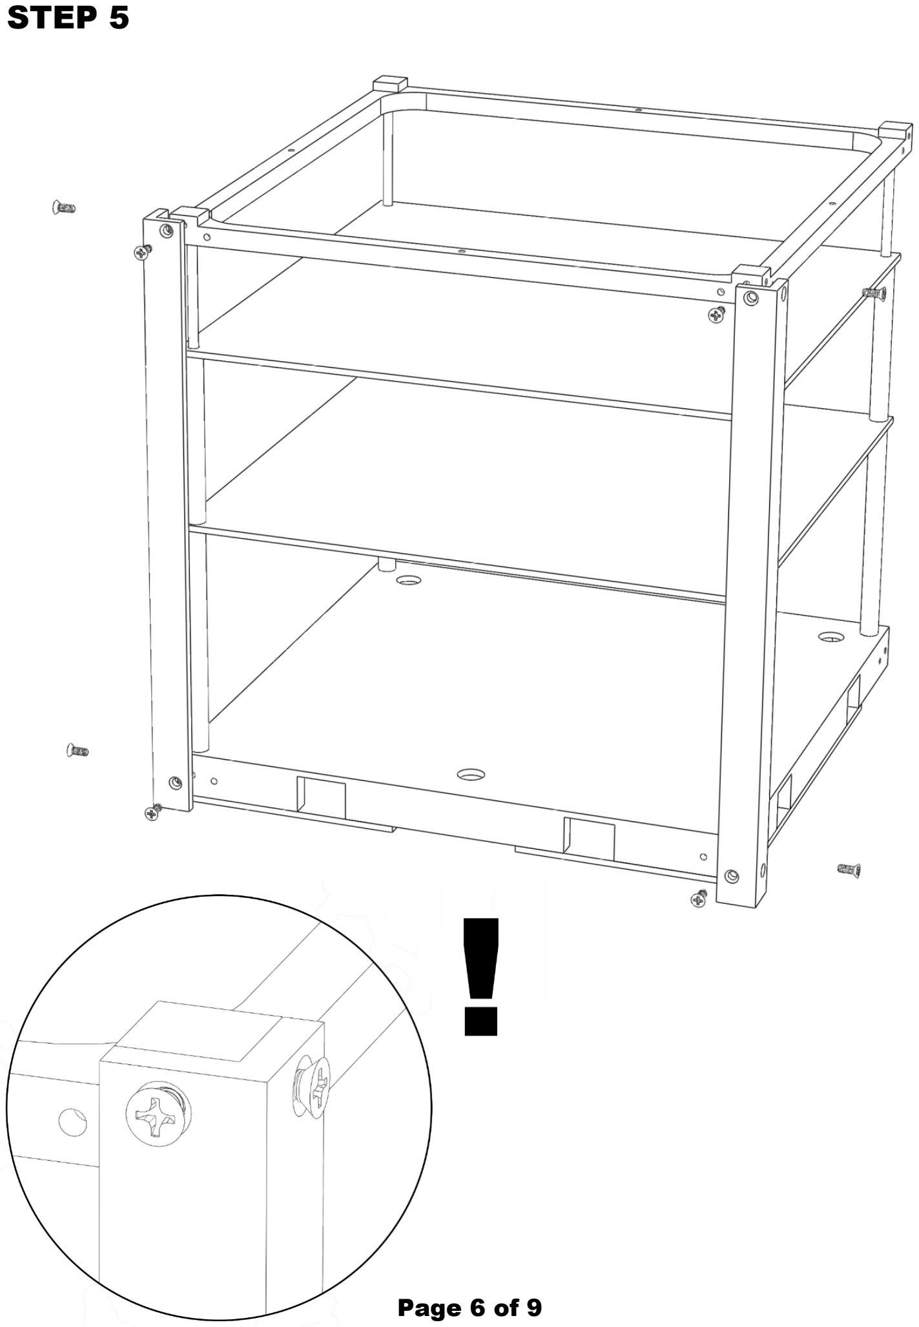
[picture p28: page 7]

Page 6 of 9

## STEP 6

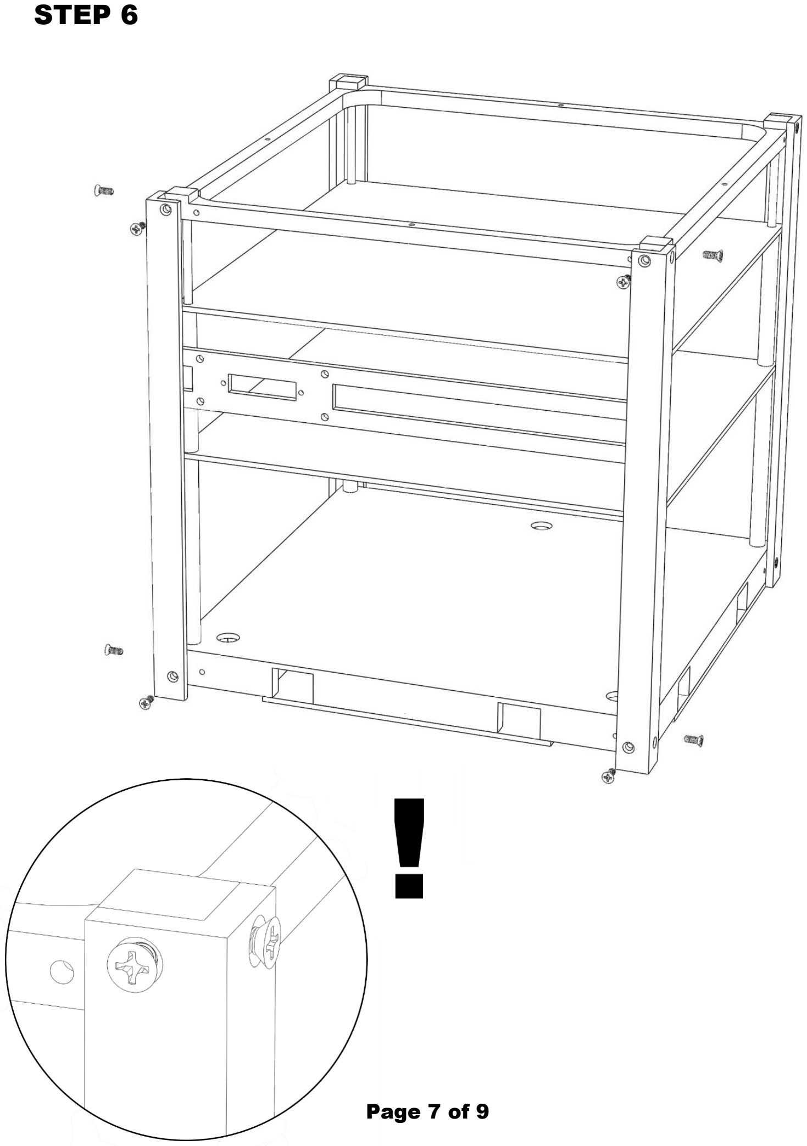
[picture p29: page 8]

Page 7 of 9

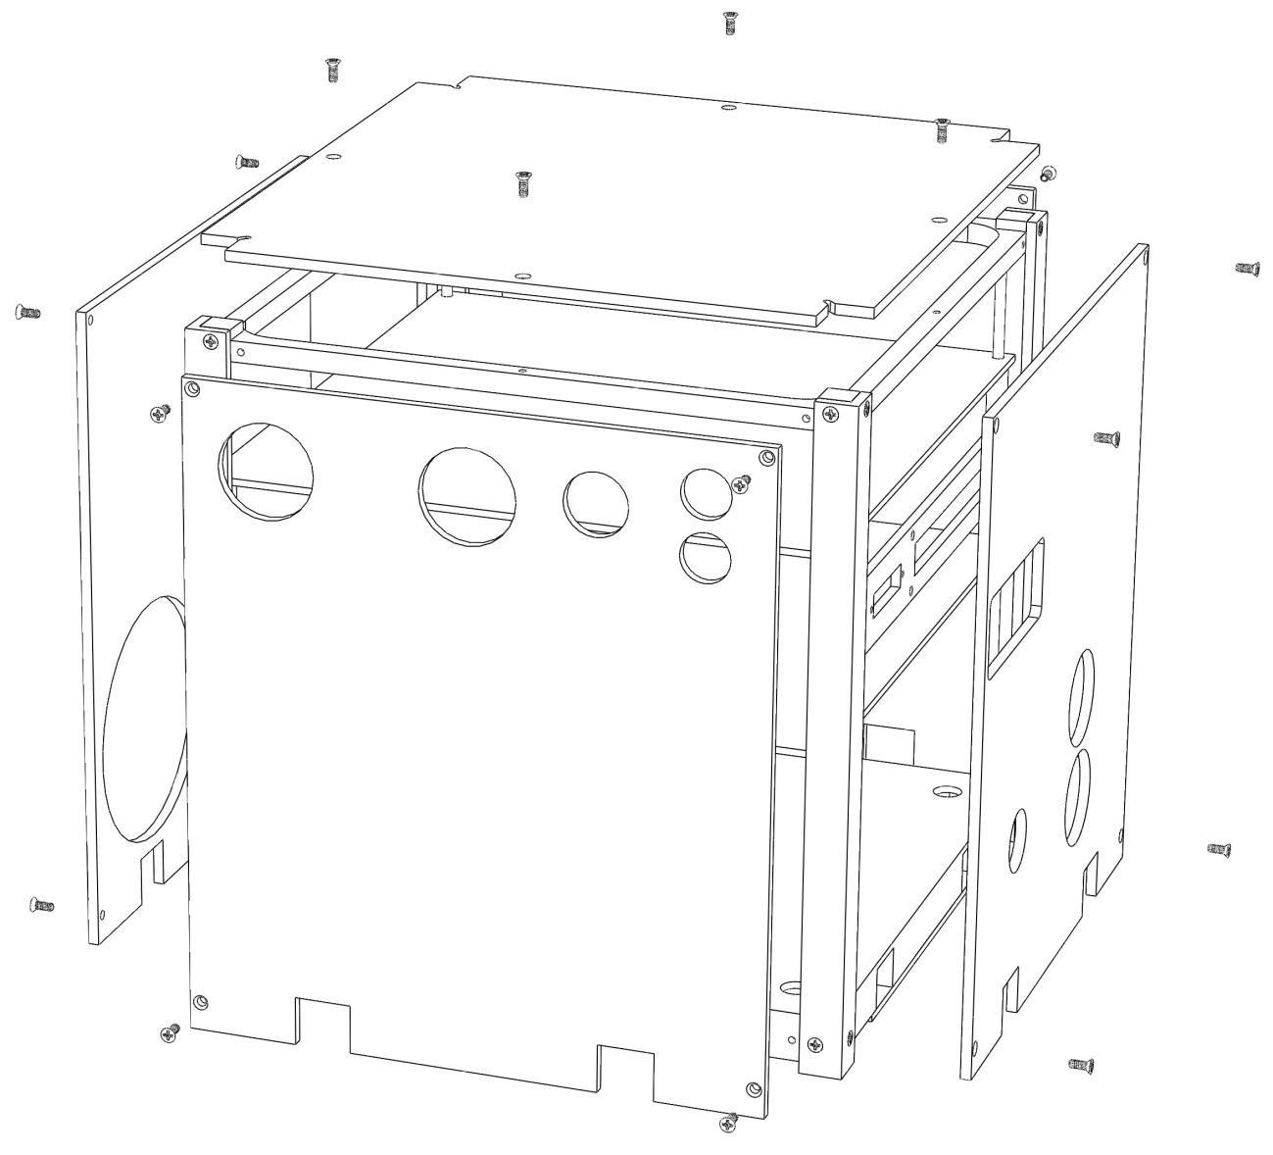
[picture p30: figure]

Page 8 of 9

## STEP 7

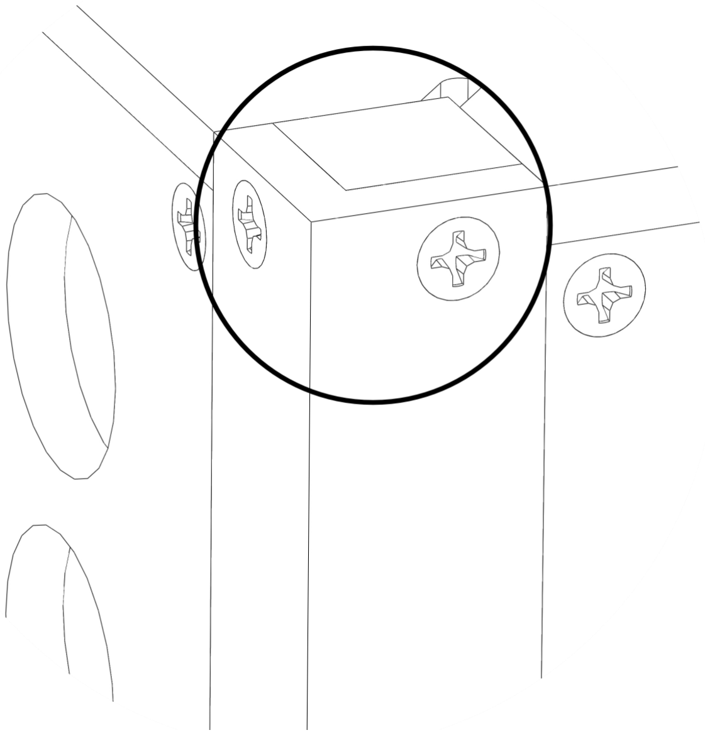
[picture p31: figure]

Page 9 of 9

## STEP 8

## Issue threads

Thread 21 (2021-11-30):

### ISSUE TITLE
Air Compressor Won't Fully Charge Tanks

### ISSUE THREAD

**Issue by TheElectricDream** [Carleton-SRCL/SPOT#21]
Significant leak present in air compressor. Prevents charging beyond 2500 PSI.

**Comment by Carleton-SRCL** [comment]
On Oct. 1st, Paul Howard from Ottawa Compressor Services (OCS) confirmed that the missing parts required for the annual maintenance (including the replacement of the faulty valve) were ordered and should arrive sometime next week.

**Comment by Carleton-SRCL** [comment]
Leak is fixed and compressor got its annual maintenance.

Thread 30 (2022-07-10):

### ISSUE TITLE
"Run Simulation" error on first attempt

### ISSUE THREAD

**Issue by c-bash** [Carleton-SRCL/SPOT#30]
**In the laboratory:** 
When the RP3s are powered on and the "Run Simulation" button is clicked for the first time in the GUI on the lab computer, MATLAB will try to update libraries on one of the Pis. It will fail out, as per the error messages below.

![runsimulation-spot3p8p0-debug-1](https://user-images.githubusercontent.com/89787972/175078027-f09bbf39-6413-4305-9d99-c47904a13ced.png)

![runsimulation-spot3p8p0-debug-2](https://user-images.githubusercontent.com/89787972/175078073-f9619396-06be-448b-9ca3-30105d107cc4.png)

Clicking "Run Simulation" a second time will be successful.

**At home:**
When working at home on a personal computer, the MATLAB tries to connect to the Pis upon clicking "Run Simulation" for the first time. It will throw the error as seen below.

![image](https://user-images.githubusercontent.com/89787972/175180596-f7eb8d7d-30a2-4ecb-830c-c1d421e127a4.png)

**Comment by TheElectricDream** [comment]
Fixed in the latest release.

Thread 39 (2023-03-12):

### ISSUE TITLE
Rewire RED Thrusters

### ISSUE THREAD

**Issue by TheElectricDream** [Carleton-SRCL/SPOT#39]
The thruster order on RED should match the other platforms.

**Comment by TheElectricDream** [comment]
Done! Unfortunately the colors do not match the other platforms but at least the GPIO layout now matches (so GPIO 10 is thruster 5 on all platforms even though the color of the wire does not match).

![image](https://user-images.githubusercontent.com/68435427/224549907-1bb5cfa6-41a1-408d-9ccd-18e7fd780e95.png)

**Comment by c-bash** [comment]
Rewired so all platform thrusters have the same 'number-colour' coding. See [electrical diagram](https://github.com/Carleton-SRCL/SPOT/wiki/Power-Subsystem) for wiring details.

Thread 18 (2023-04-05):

### ISSUE TITLE
Robotic Arm LEDs Connectors Need Labels

### ISSUE THREAD

**Issue by TheElectricDream** [Carleton-SRCL/SPOT#18]
The LED female-male connectors do not have any labels on the ports. Right now, connecting them is trial and error. Someone should label them.

**Comment by Carleton-SRCL** [comment]
Parker should look into it this summer.

**Comment by Kirkados** [comment]
TBD on whether this is needed anymore, as the arm joint encoders can now be read in real-time

**Comment by TheElectricDream** [comment]
When I read the encoder values in the lab there are a ton of data drops in the encoder data. Was that what you experienced?

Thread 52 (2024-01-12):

### ISSUE TITLE
Upgrade Drain Tubes on Air Compressor

### ISSUE THREAD

**Issue by c-bash** [Carleton-SRCL/SPOT#52]
Air compressor: Current drain tubes for points B and C are cracking and quite short with liquid currently being collected by a plastic water bottle. 

An upgrade is required such that the drain tubes are replaced and, ideally, not pointing directly at the platforms. A more semi-permanent collection basin should be at the end of the tubes.

**Comment by Kirkados** [comment]
Perhaps an elbow could run drain tubes down towards the floor where an absorbent material (like a dog pee pad?) absorbs the ejected moisture.

**Comment by TheElectricDream** [comment]
A pro tip as well, I've stopped using the bottle and I use a bundle of shop towels to catch the liquid. Just less gross that way.

**Comment by c-bash** [comment]
This has been completed! In future, we likely want to move the drain box to a better location since currently it blocks the bottom right drawer. 

![IMG_4292 17060](https://github.com/Carleton-SRCL/SPOT/assets/89787972/3297a6b6-9f33-417d-9535-a42f0de10c7e)

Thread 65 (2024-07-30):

### ISSUE TITLE
Add Orientation Labels to the Platform Tops

### ISSUE THREAD

**Issue by TheElectricDream** [Carleton-SRCL/SPOT#65]
Add a label to the inside of platform tops (that have the LED) to indicate the correct orientation. Open to other ideas.

**Comment by c-bash** [comment]
Spoke with Steve, and we think that the best way forward is to have the orientation engraved on the platform tops. Perhaps something like "Control Panel This Way" on the side with the control panel. Would it also be beneficial for students/researchers to engrave the +X and +Y directions of the body frame on the platform tops?

**Comment by TheElectricDream** [comment]
That would certainly look more professional, I'm all for it

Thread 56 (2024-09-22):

### ISSUE TITLE
SPOT GUI Indicates (0,0,0) for Platforms Positions, but LEDs Stay On

### ISSUE THREAD

**Issue by TheElectricDream** [Carleton-SRCL/SPOT#56]
I believe the issue is caused by the PhaseSpace program that sends the data crashing in the background. This would result in the LEDs being on (PhaseSpace initialized), but there is no UDP to send the data, and the GUI is stuck in a pseudo-functional state. I can add a check in the GUI to record the ID of the PhaseSpace executable when it is started, and then I can check that it is still running every couple of seconds. If it crashed, I can toggle the GUI PhaseSpace switch to OFF to properly shut down the PhaseSpace cameras and then I can provide a warning to the user to simply "try again".

**Comment by TheElectricDream** [comment]
The current workaround is to restart the ground station computer.

**Comment by c-bash** [comment]
Another potential fix is to replace the StreamData.exe file in your current project to the most up-to-date version [found on the wiki](https://github.com/Carleton-SRCL/SPOT/blob/main/Template_Files/Resources/StreamData.exe)

**Comment by TheElectricDream** [comment]
Resolved in [4.1](https://github.com/Carleton-SRCL/SPOT/releases/tag/4.1.0-prerelease.1)

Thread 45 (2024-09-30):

### ISSUE TITLE
Create a comprehensive Wiki section on Computer Vision

### ISSUE THREAD

**Issue by Carleton-SRCL** [Carleton-SRCL/SPOT#45]
User guide type of section on Wiki that explains, in a step-by-step approach, how to develop, implement, interface with sensors, test, and deploy in experiments basic computer vision software.

**Comment by TheElectricDream** [comment]
I am fairly confident that this is complete, or at least most of the way there, thanks to @NerdAlert57. Going to close this for now.

https://github.com/Carleton-SRCL/SPOT/wiki/Getting-Started-with-Computer-Vision

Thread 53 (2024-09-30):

### ISSUE TITLE
Bug Fixes and Improvements for Eventual 4.1 Release (Post-Capstone)

### ISSUE THREAD

**Issue by TheElectricDream** [Carleton-SRCL/SPOT#53]
The warning message headers and message still refer to the Raspberry Pi, so this needs to be updated for the next software release.

![image](https://github.com/Carleton-SRCL/SPOT/assets/68435427/31415410-a922-427c-b3bc-d041178adb44)

**Comment by TheElectricDream** [comment]
- Remove a leftover termination block I found in the "Check Connections" subsystem.
- Update version numbers to 4.1 and modify the warning message on startup to check for R2023a and R2023b.
- Update the default SPOT GUI mat file to correct some mistakes and ensure compatibility with 4.1.

**Comment by TheElectricDream** [comment]
- As indicated by Steve, it would be great if we could make the connection LED update in real-time to notify users if there is a drop in the connection status. This could be done by having a function ping the platforms every minute or so. This change would have to be done in a way that does not freeze the rest of the GUI.

**Comment by TheElectricDream** [comment]
- Try a heuristic-based approach for the control mixer to improve results.
- Investigate alternative controllers (or implement best capstone controller) to find new default controller. Should be simple enough for future researchers but not so complex as to cause confusion.

**Comment by TheElectricDream** [comment]
- In the real-time viz, it should show the current time for the experiment somewhere.
- There should be a button to refresh the list of available Simulink diagrams so that you don't need to restart the GUI when you make a new diagram.

**Comment by c-bash** [comment]
- Move BLACK's magnet gate control wire from 3.3V to a GPIO on the Xavier NX. Add functionality in the GUI to toggle this GPIO pin so that we can detach the magnets without turning off power to BLACK.

**Comment by TheElectricDream** [comment]
Fix the incorrect labels in the data logging subsection of the simulink template.

**Comment by TheElectricDream** [comment]
This list is now closed with the release of SPOT 4.1 Pre-Release.1, available for download here: https://github.com/Carleton-SRCL/SPOT/releases/tag/4.1.0-prerelease.1-hotfix.1

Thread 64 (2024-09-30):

### ISSUE TITLE
Add Wiki Entry Regarding Mac OS Compatibility

### ISSUE THREAD

**Issue by TheElectricDream** [Carleton-SRCL/SPOT#64]
Title is self-explanatory

**Comment by adamvigneron** [comment]
First, the easy one -- Mac OS paths use the forward slash, Windows paths use the backward slash.

Affected files:
``Setup_Environment.m``
``GUI_v4_0_Main.mlapp``

One possible fix is to replace all path-related uses of backslash with the ``filesep`` command:
[filesep in MATLAB](https://www.mathworks.com/help/matlab/ref/filesep.html)

Also possible to build paths using the ``fullfile`` command:
[fullfile in MATLAB](https://www.mathworks.com/help/matlab/ref/fullfile.html)

...according to this thread, we could just YOLO and only use forward slashes:
[forward slash thread](https://www.mathworks.com/matlabcentral/answers/117110-dealing-with-and-windows-vs-unix-for-path-definition)

**Comment by adamvigneron** [comment]
Second, as the NVIDIA add-on isn't currently supported for Mac OS, experiments are not possible AND simulations need a few more things commented out:

``GUI_v4_0_Main.mlapp``, lines 1973 and 1999
the project ``*.slx`` file, blocks corresponding to experiment logic and the NVIDIA interface.

A detailed list will be maintained on the wiki.

**Comment by adamvigneron** [comment]
@TheElectricDream , let's see how we can do this in an efficient manner.

Per the comments above, I've made changes to three files:
``SetupEnvironment.m``
``GUI_v4_0_Main.mlapp``
``BetaMacs.slx`` (my project copy of the template)

I've pushed the changes to my SPOT fork:
https://github.com/adamvigneron/AdamVigneron-SPOT/commit/2eeefe4f9d93ccc0c31c05fe6068f345f108d513

where it's possible to see the plaintext M-file changes but not possible to see the binary changes.  Luckily, the binary files can be compared to their ``Template_Files/``equivalents using MATLAB functionality for File Compare.

How do you want to go about capturing this in the wiki?
How do you want to go about capturing this in the codebase?

**Comment by TheElectricDream** [comment]
I have create a Wiki entry on this subject here: https://github.com/Carleton-SRCL/SPOT/wiki/Regarding-MacOS-Compatibility

However, we will not be creating and supporting a MacOS compatible diagram - I do not have a MacOS system available and the lab stance is that it should not be used with SPOT. I've entered the steps as you laid out in the Wiki entry, but these steps may change with future versions and I will not dedicate time to keeping those steps up to date. Users who are simply MUST use MacOS should expect to be on their own and will need to sort out compatibility on a case-by-case basis.

**Comment by adamvigneron** [comment]
The wiki entry looks great, thanks Alex!

As discussed, there are two additional code snippets we could add to GUI_v4_0_Main.mlapp:

```
if ismac
    fprintf('GUI_v4_0_Main.StartSimulationButtonPushed:\n');
    fprintf('  MATLAB Coder for NVIDIA unavailable on Mac OS;\n');
    fprintf('  pre-simulation switch of HardwareBoard disabled.\n\n')
else
    set_param(activeConfigObj,'HardwareBoard','None');
end
```

```
if ismac
    fprintf('GUI_v4_0_Main.StartSimulationButtonPushed:\n');
    fprintf('  MATLAB Coder for NVIDIA unavailable on Mac OS;\n');
    fprintf('  post-simulation switch of HardwareBoard disabled.\n\n')
else
    set_param(activeConfigObj,'HardwareBoard','NVIDIA Jetson');
end
```

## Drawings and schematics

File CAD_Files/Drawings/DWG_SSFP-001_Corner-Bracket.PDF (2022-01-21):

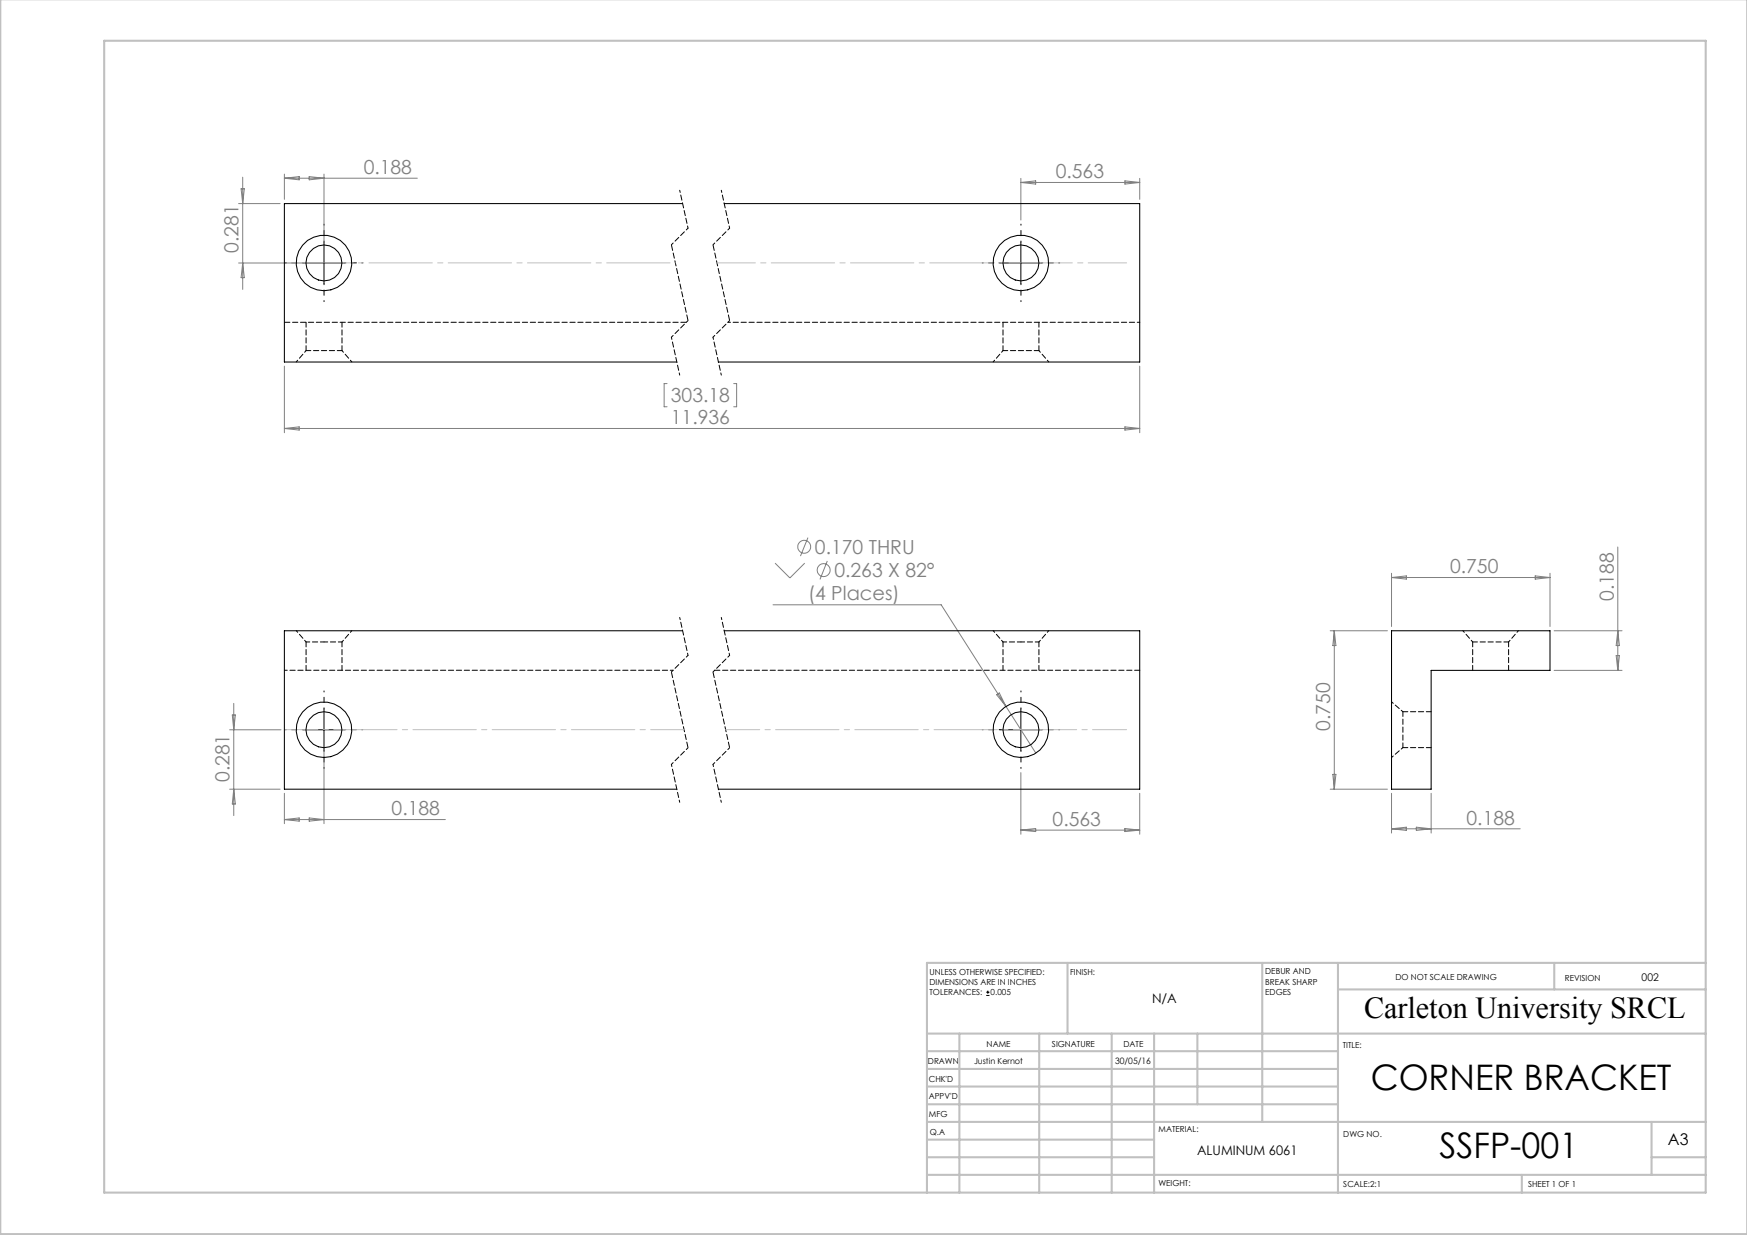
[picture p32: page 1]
0.170 THRU 0.263 X 82° (4 Places); SCALE:2:1; SHEET 1 OF 1; DO NOT SCALE DRAWING; REVISION; UNLESS OTHERWISE SPECIFIED:; FINISH:

DIMENSIONS ARE IN INCHES
TOLERANCES: 0.005

DEBUR AND
BREAK SHARP
EDGES
Carleton University SRCL

NAME | SIGNATURE | DATE | | | | TITLE: CORNER BRACKET
Q.A | | | | MATERIAL: ALUMINUM 6061 | SSFP-001 DWG NO. | A3

DRAWN | Justin Kernot | | 30/05/16
CHK'D
APPV'D
MFG

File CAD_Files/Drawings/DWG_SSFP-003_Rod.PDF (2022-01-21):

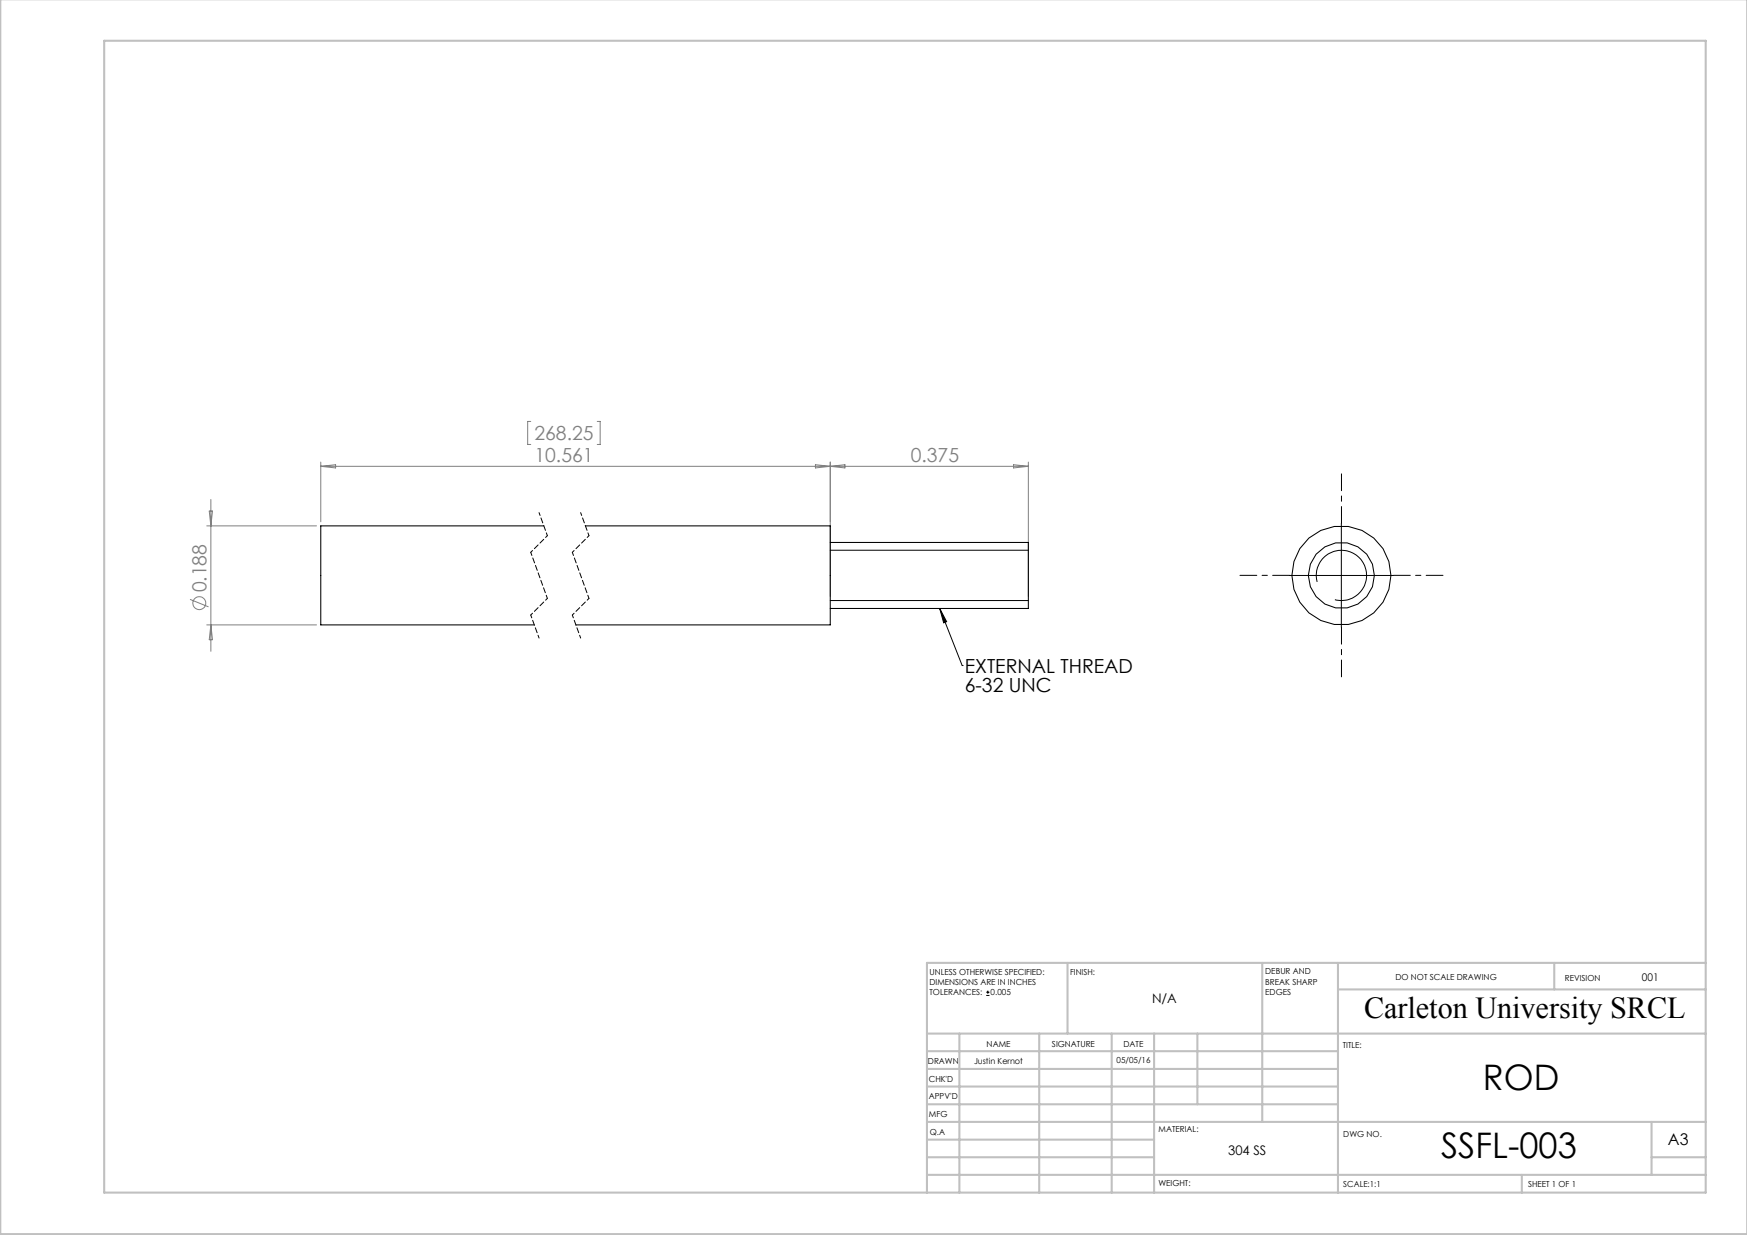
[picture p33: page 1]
EXTERNAL THREAD 6-32 UNC; SCALE:1:1; SHEET 1 OF 1; DO NOT SCALE DRAWING; REVISION; UNLESS OTHERWISE SPECIFIED:; FINISH:

DIMENSIONS ARE IN INCHES
TOLERANCES: 0.005

DEBUR AND
BREAK SHARP
EDGES
Carleton University SRCL

NAME | SIGNATURE | DATE | | | | TITLE: ROD
Q.A | | | | MATERIAL: 304 SS | SSFL-003 DWG NO. | A3

DRAWN | Justin Kernot | | 05/05/16
CHK'D
APPV'D
MFG

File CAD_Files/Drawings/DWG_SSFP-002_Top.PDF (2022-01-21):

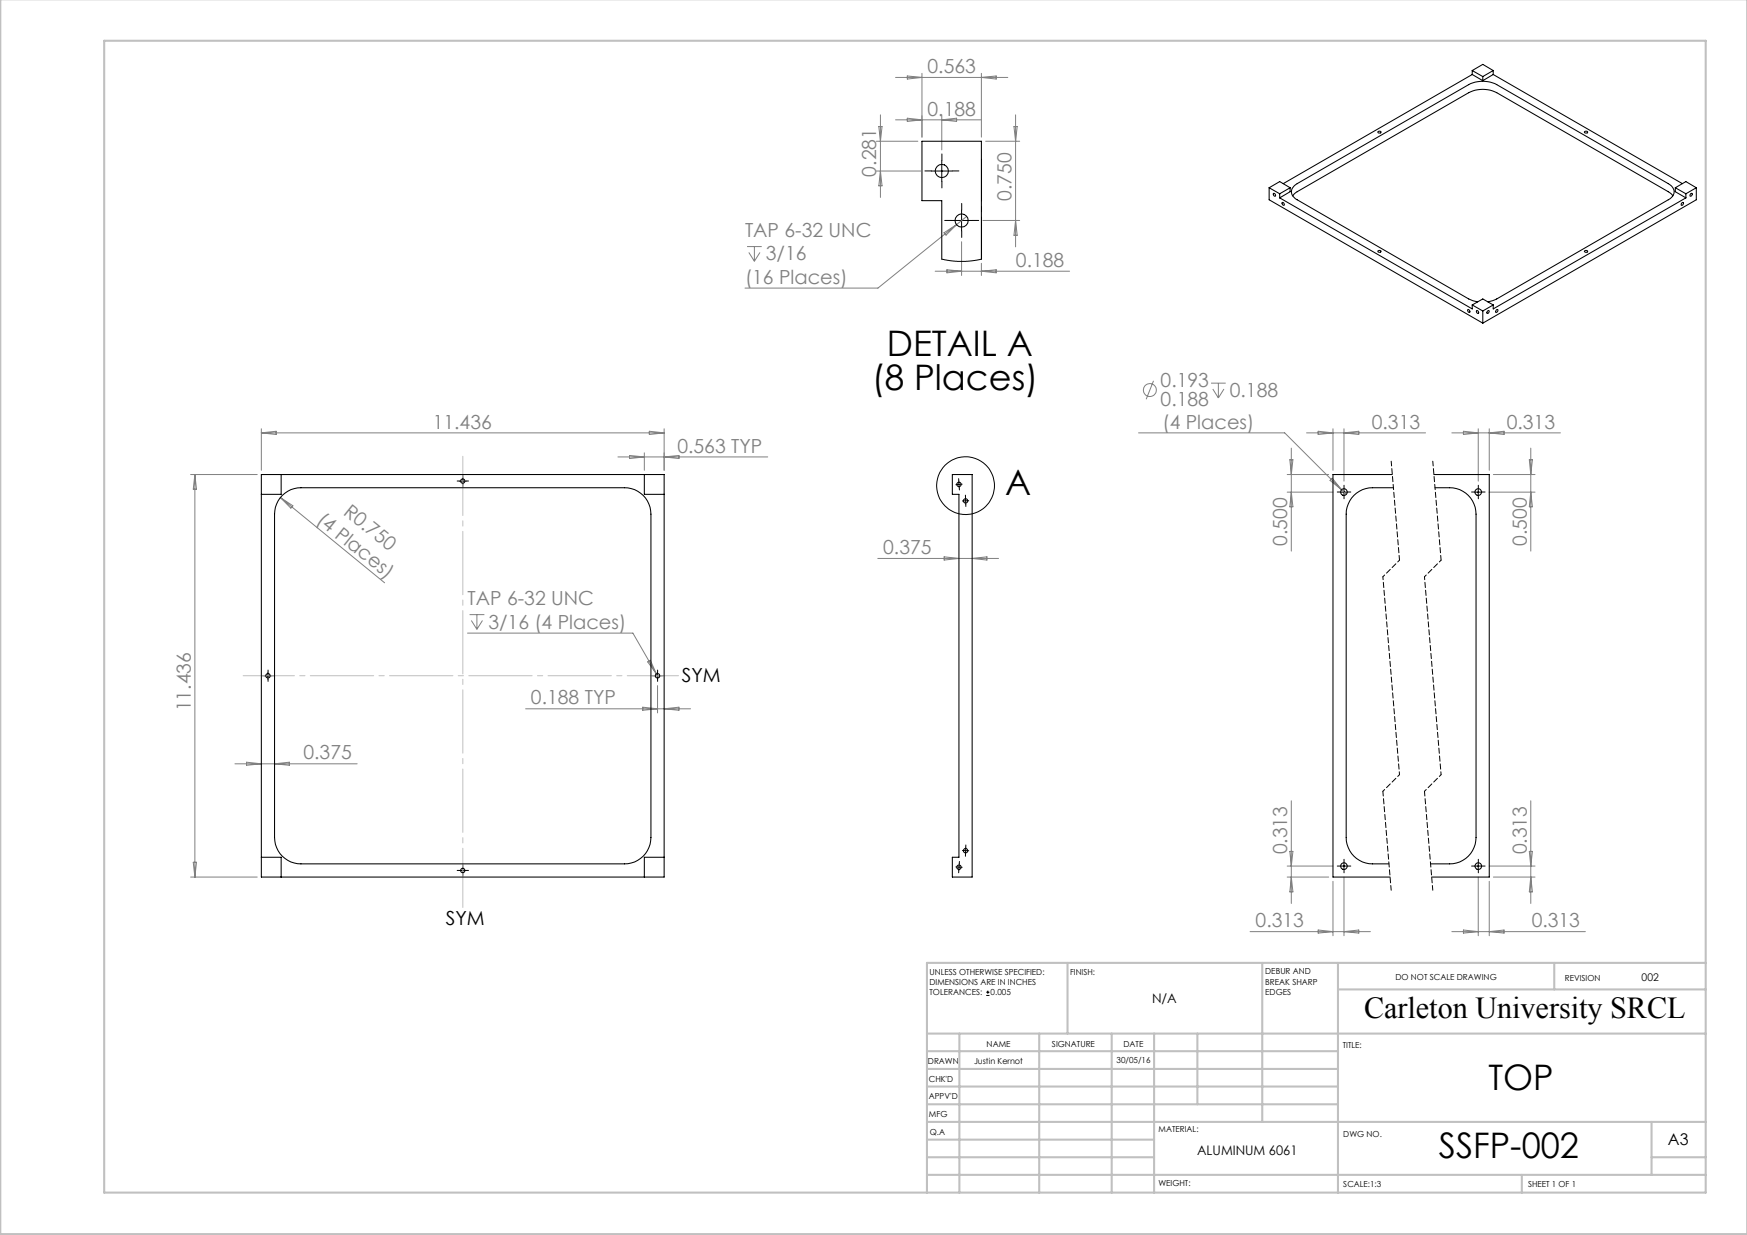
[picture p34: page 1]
0.188 0.188 (4 Places); 0.563 TYP; TAP 6-32 UNC 3/16 (4 Places); (4 Places); 0.188 TYP; TAP 6-32 UNC; (16 Places); DETAIL A (8 Places); SCALE:1:3; SHEET 1 OF 1; DO NOT SCALE DRAWING; REVISION; UNLESS OTHERWISE SPECIFIED:; FINISH:

DIMENSIONS ARE IN INCHES
TOLERANCES: 0.005

DEBUR AND
BREAK SHARP
EDGES
Carleton University SRCL

NAME | SIGNATURE | DATE | | | | TITLE: TOP
Q.A | | | | MATERIAL: ALUMINUM 6061 | SSFP-002 DWG NO. | A3

DRAWN | Justin Kernot | | 30/05/16
CHK'D
APPV'D
MFG

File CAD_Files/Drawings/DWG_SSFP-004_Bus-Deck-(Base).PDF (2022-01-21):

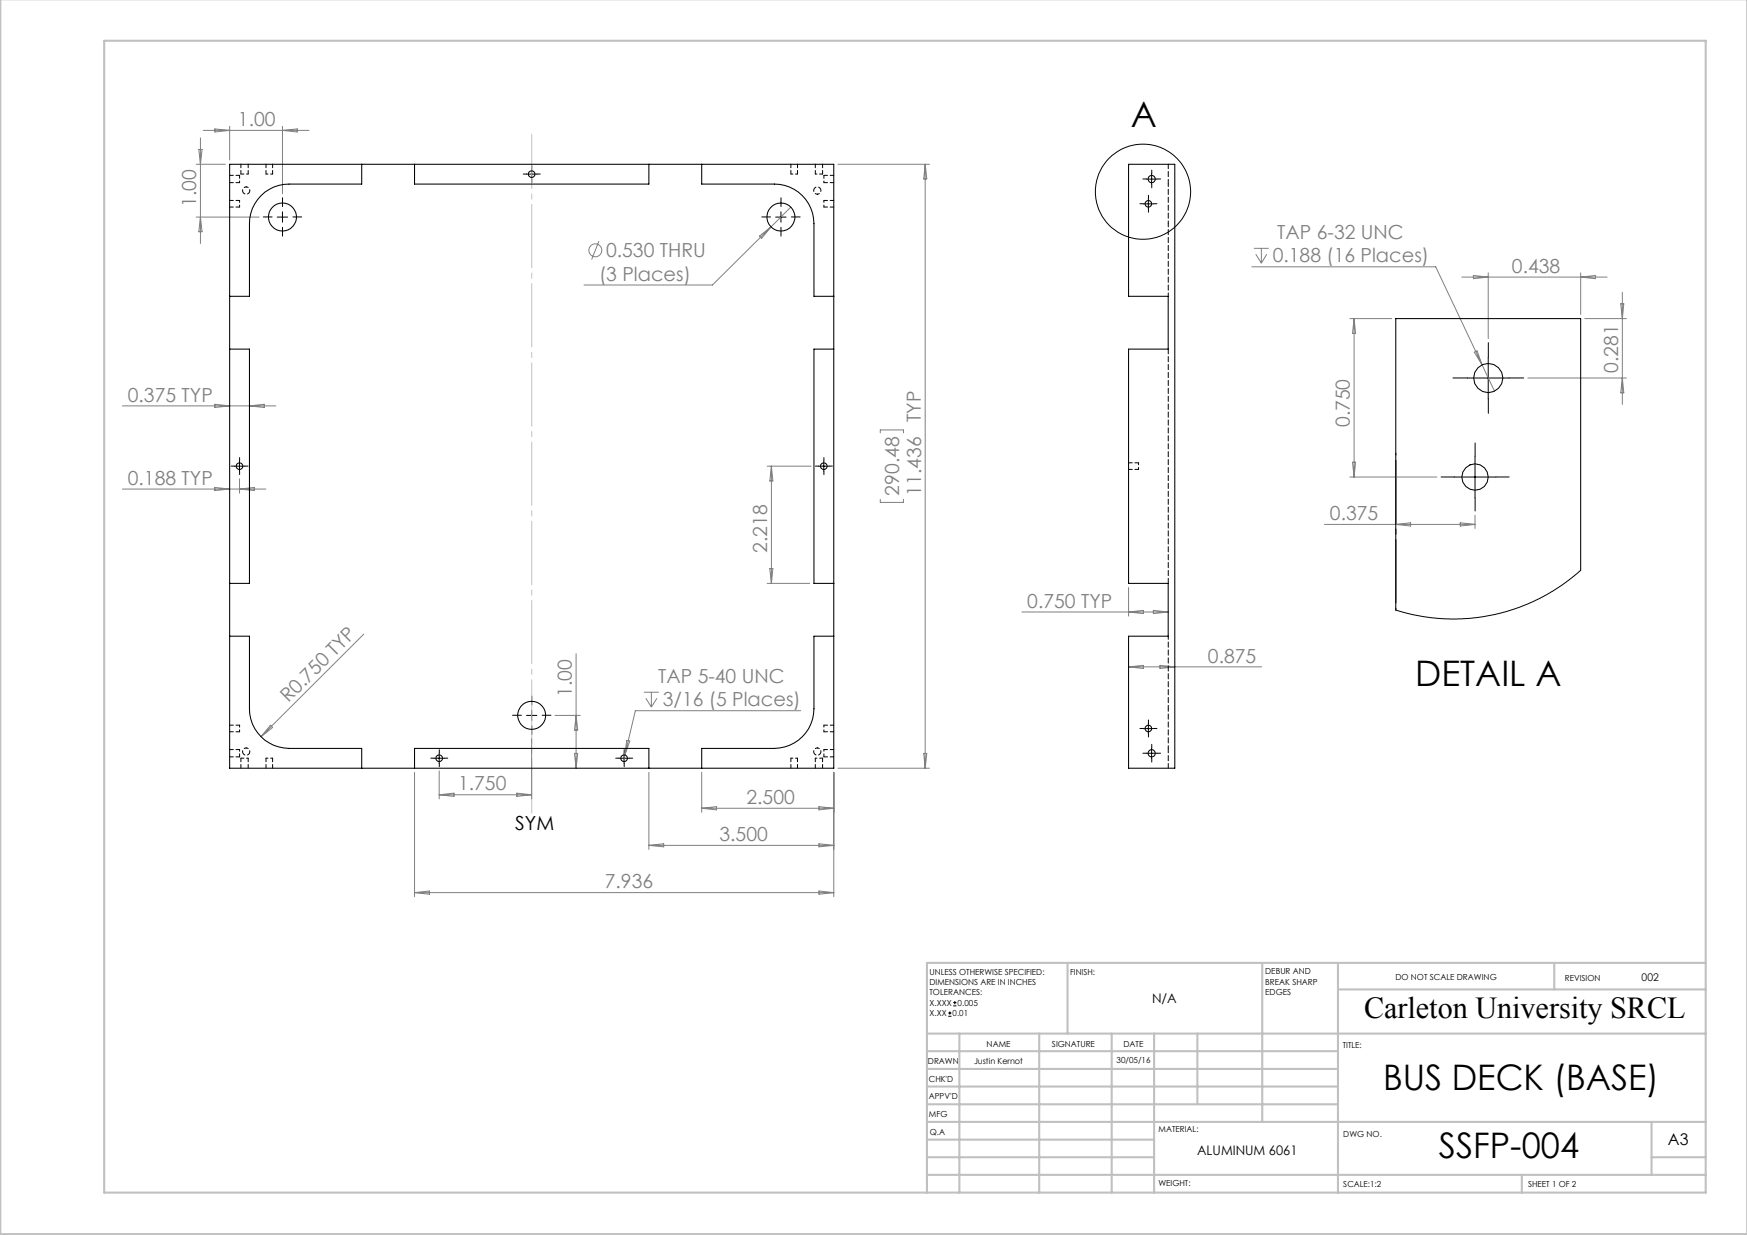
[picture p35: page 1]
11.436 TYP; 0.375 TYP; R0.750 TYP; TAP 5-40 UNC 3/16 (5 Places); 0.530 THRU (3 Places); 0.188 TYP; 0.750 TYP; TAP 6-32 UNC 0.188 (16 Places); DETAIL A; SCALE:1:2; SHEET 1 OF 2; DO NOT SCALE DRAWING; REVISION; UNLESS OTHERWISE SPECIFIED:; FINISH:

DIMENSIONS ARE IN INCHES
TOLERANCES:
X.XXX 0.005

DEBUR AND
BREAK SHARP
EDGES
Carleton University SRCL

NAME | SIGNATURE | DATE | | | | TITLE: BUS DECK (BASE)
Q.A | | | | MATERIAL: ALUMINUM 6061 | SSFP-004 DWG NO. | A3

DRAWN | Justin Kernot | | 30/05/16
CHK'D
APPV'D
MFG

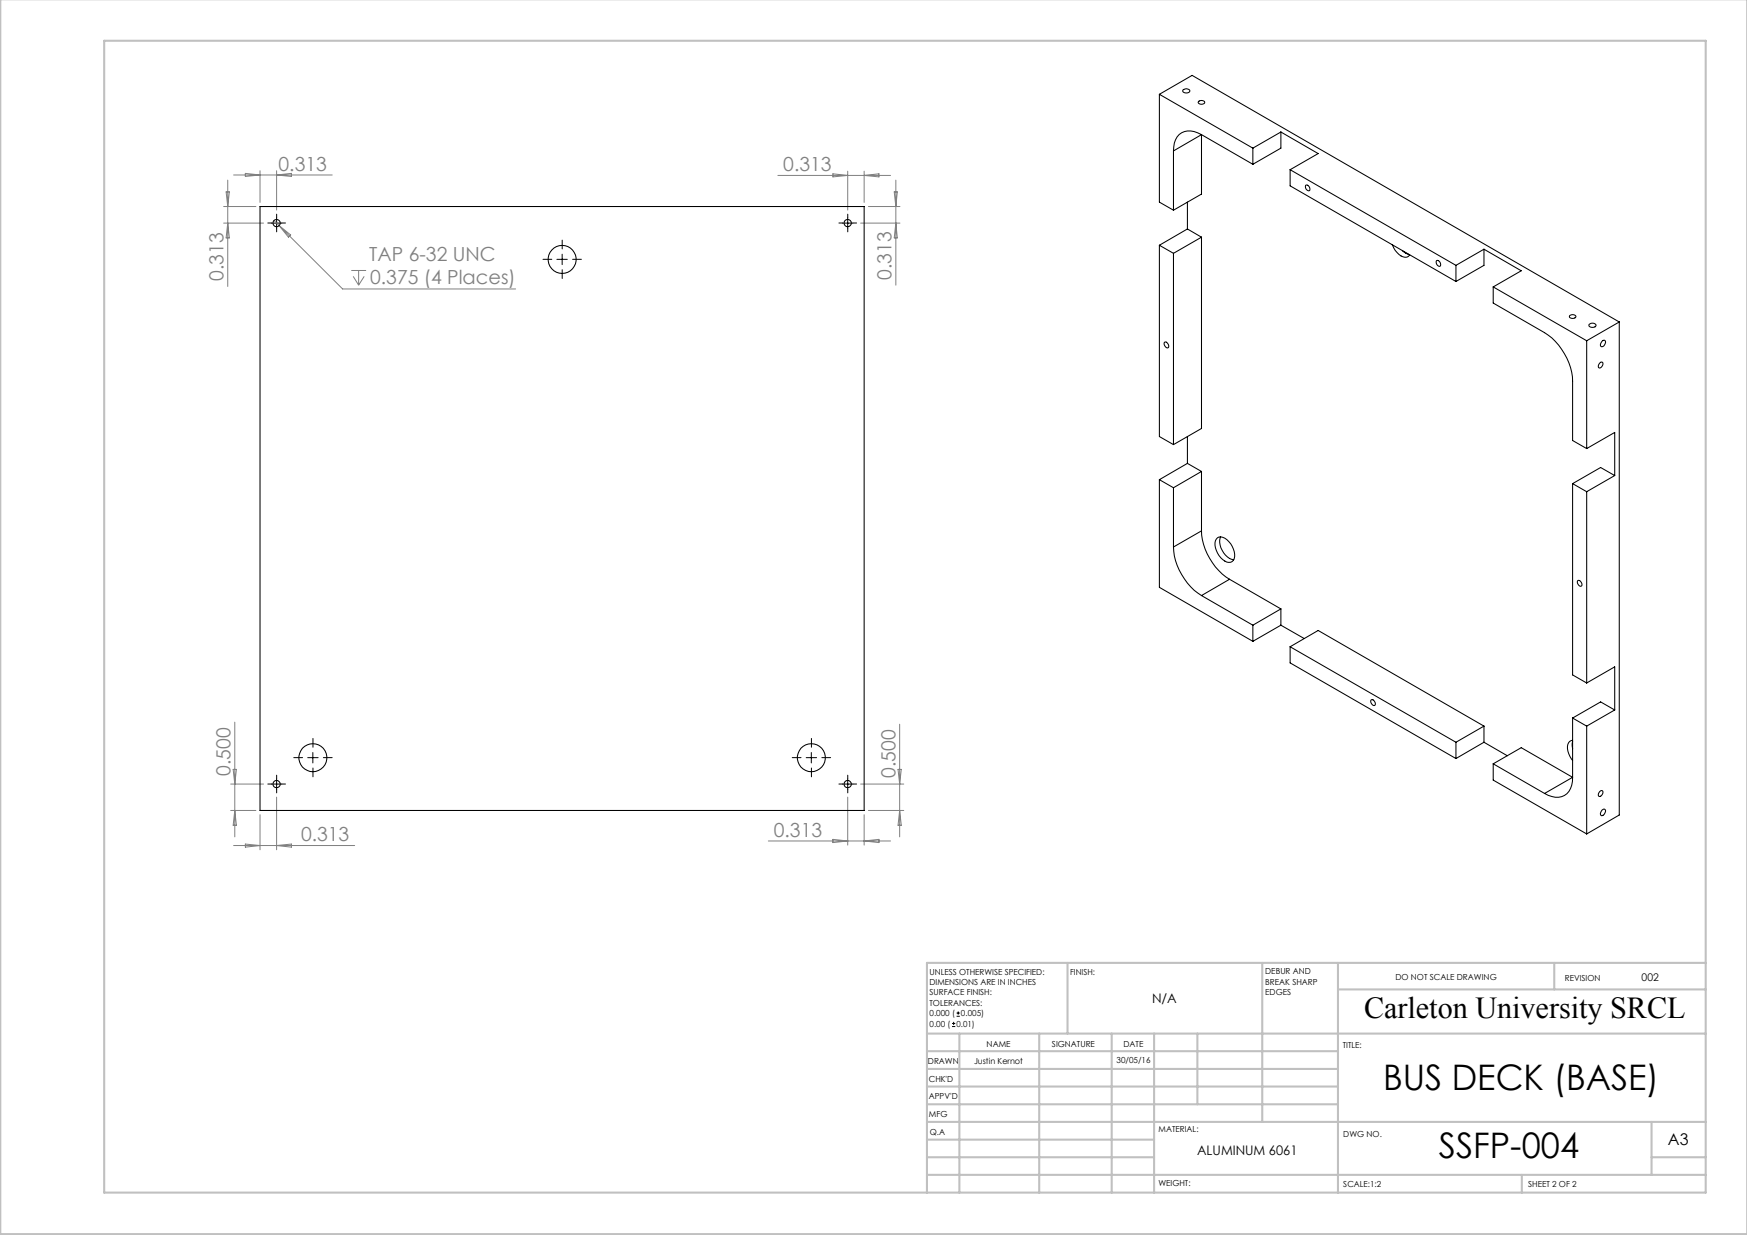
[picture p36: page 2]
TAP 6-32 UNC 0.375 (4 Places); SCALE:1:2; SHEET 2 OF 2; DO NOT SCALE DRAWING; REVISION; UNLESS OTHERWISE SPECIFIED:; FINISH:; DIMENSIONS ARE IN INCHES SURFACE FINISH:

DEBUR AND
BREAK SHARP
EDGES
Carleton University SRCL

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

DRAWN | Justin Kernot | | 30/05/16
CHK'D
APPV'D
MFG

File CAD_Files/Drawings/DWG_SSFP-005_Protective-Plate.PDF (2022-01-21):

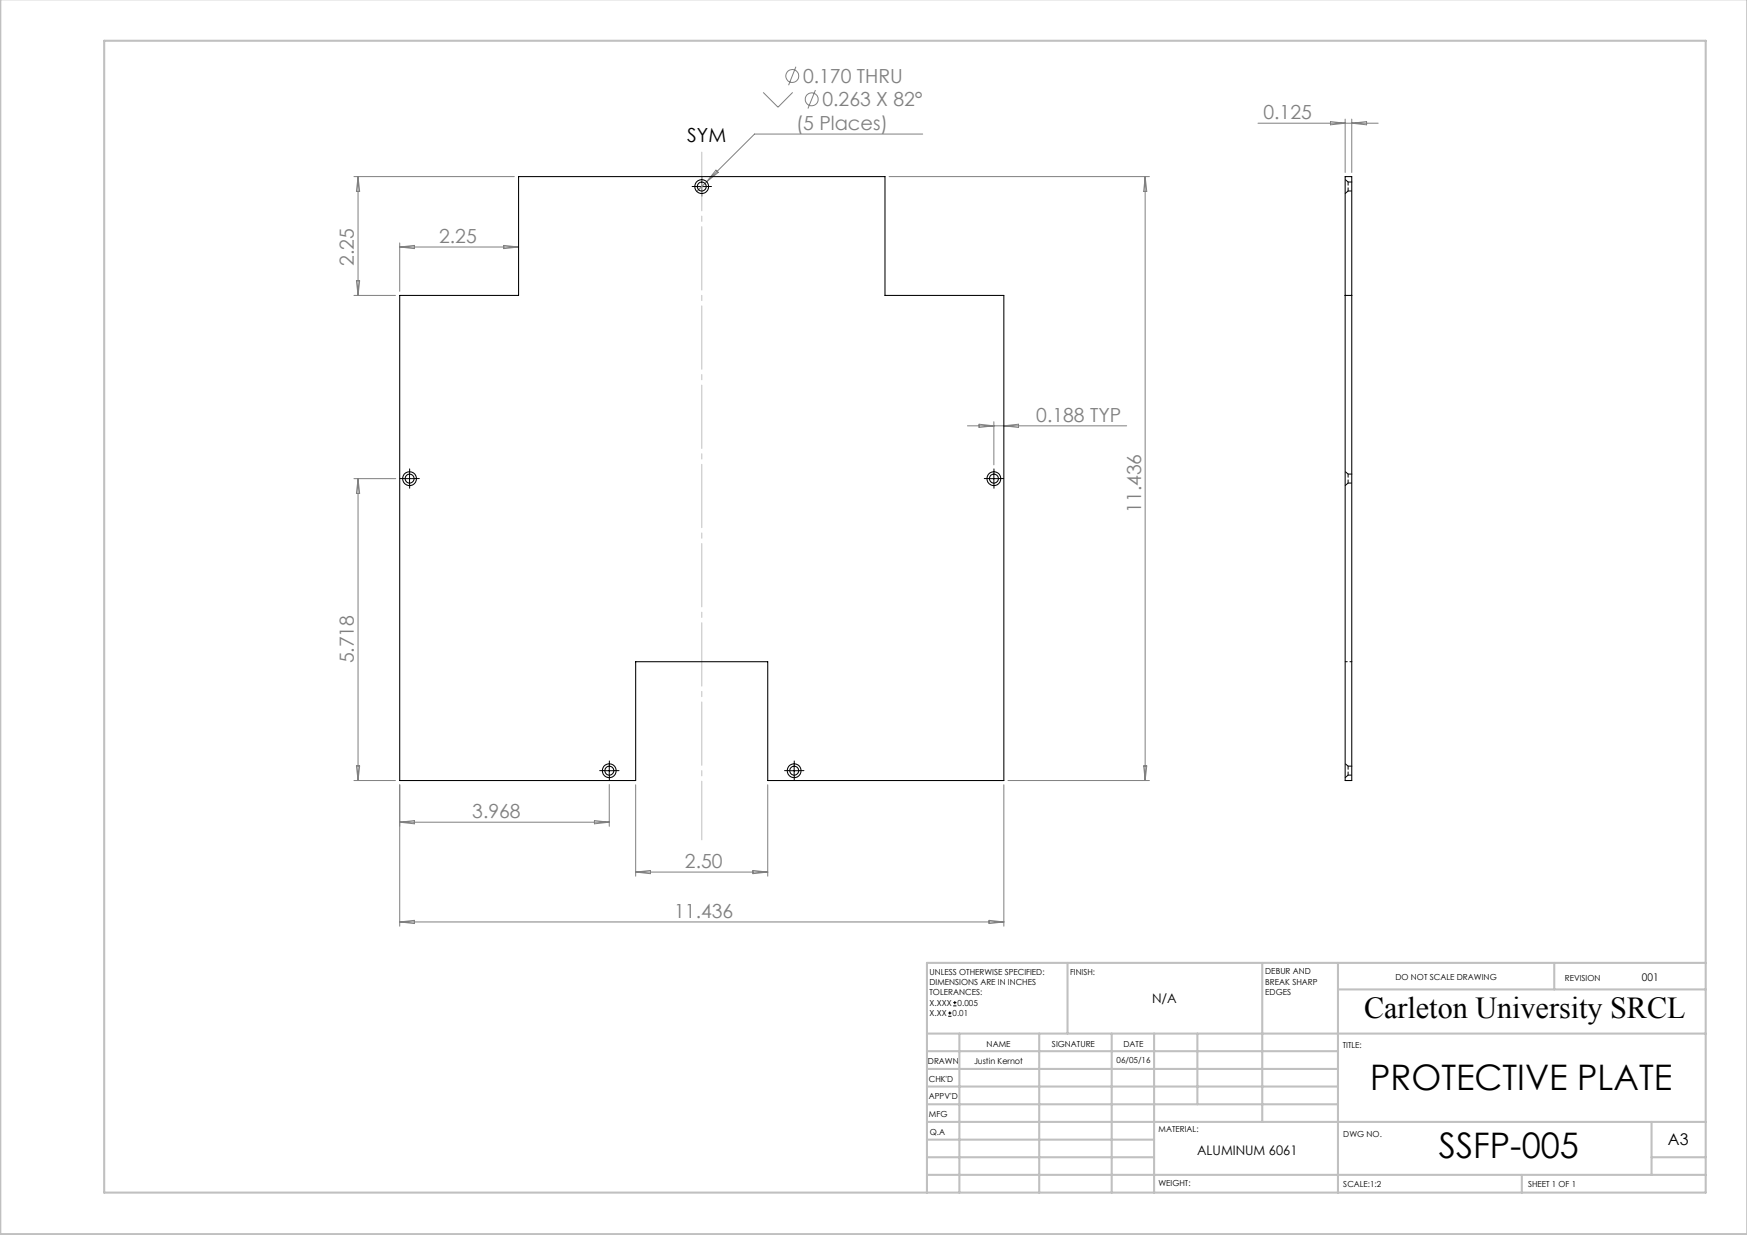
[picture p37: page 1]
0.188 TYP; 0.170 THRU 0.263 X 82° (5 Places) SYM; SCALE:1:2; SHEET 1 OF 1; DO NOT SCALE DRAWING; REVISION; UNLESS OTHERWISE SPECIFIED:; FINISH:

DIMENSIONS ARE IN INCHES
TOLERANCES:
X.XXX 0.005

DEBUR AND
BREAK SHARP
EDGES
Carleton University SRCL

NAME | SIGNATURE | DATE | | | | TITLE: PROTECTIVE PLATE
Q.A | | | | MATERIAL: ALUMINUM 6061 | SSFP-005 DWG NO. | A3

DRAWN | Justin Kernot | | 06/05/16
CHK'D
APPV'D
MFG

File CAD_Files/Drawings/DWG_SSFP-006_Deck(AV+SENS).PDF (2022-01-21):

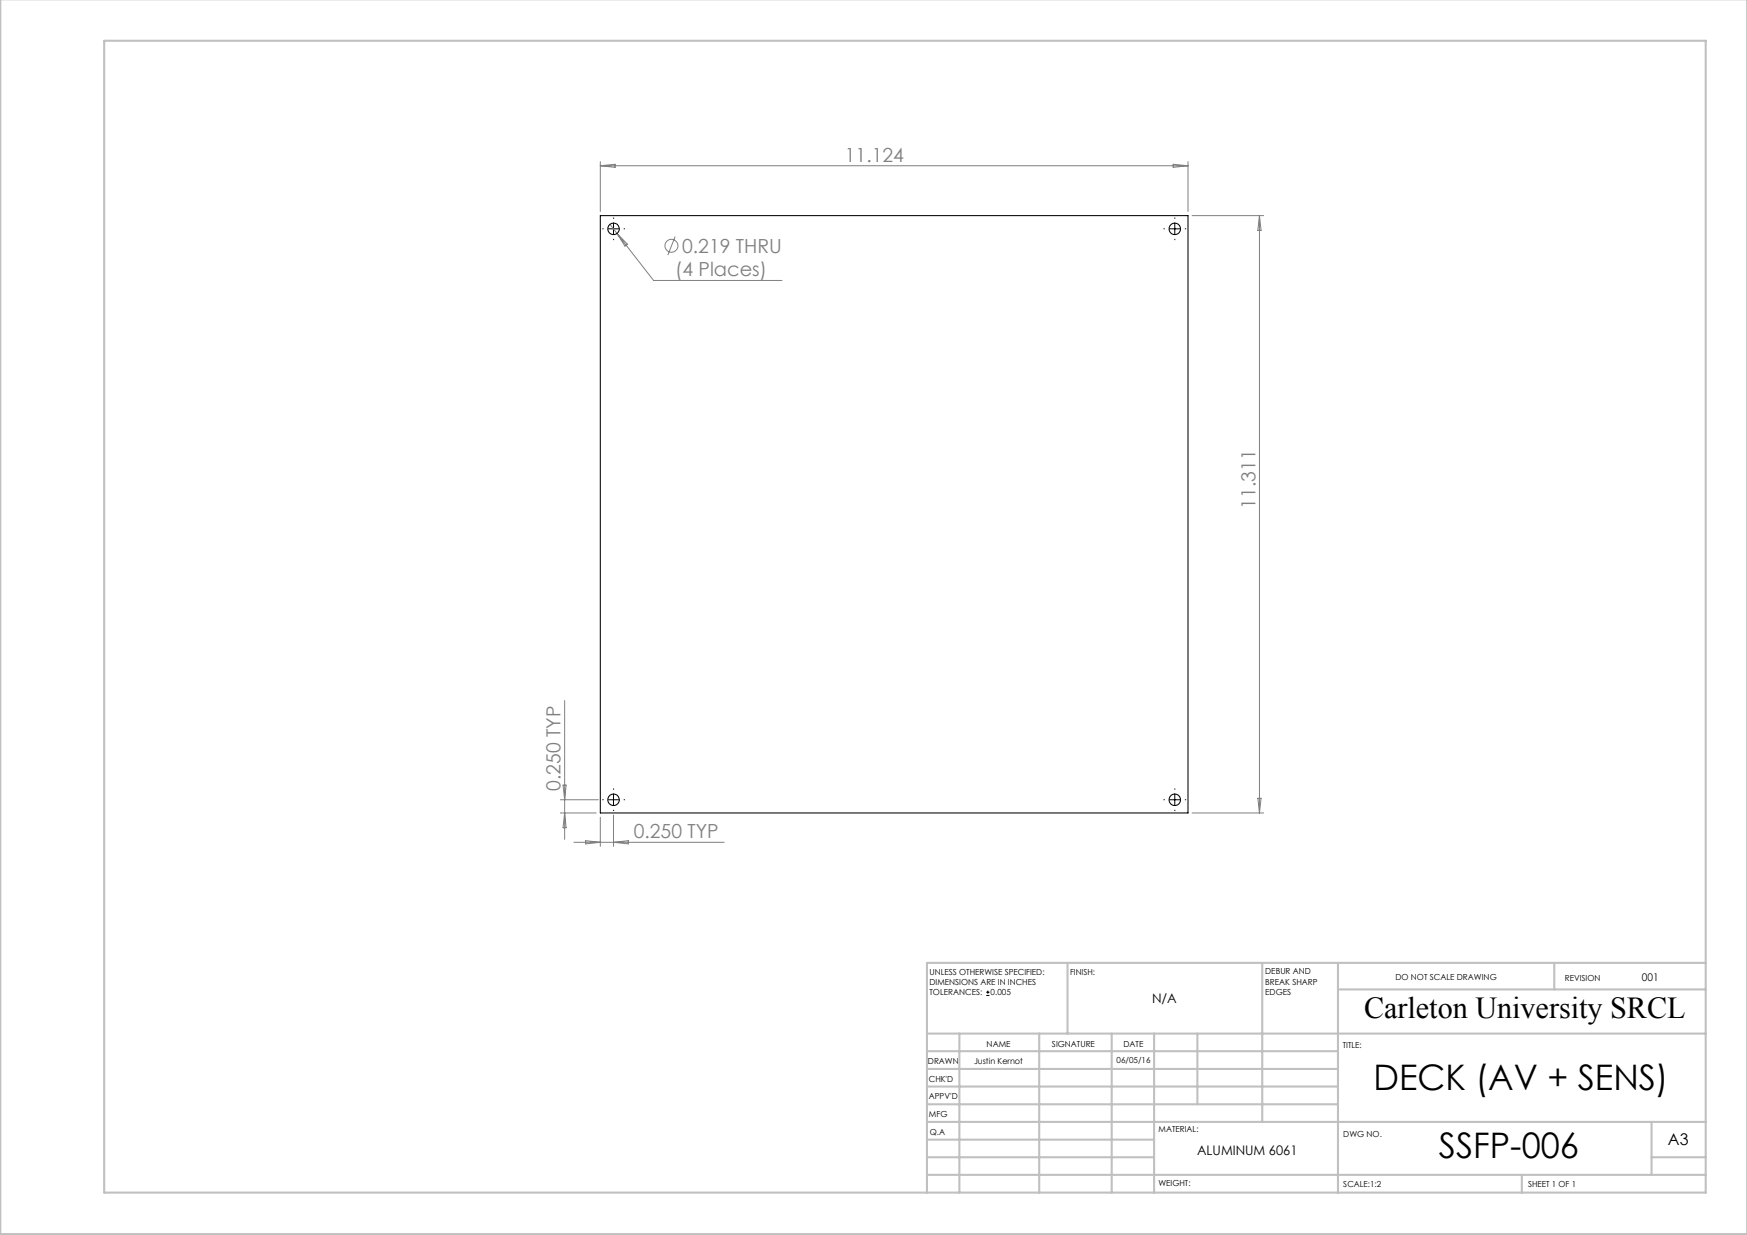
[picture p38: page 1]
0.219 THRU (4 Places); 0.250 TYP; SCALE:1:2; SHEET 1 OF 1; DO NOT SCALE DRAWING; REVISION; UNLESS OTHERWISE SPECIFIED:; FINISH:

DIMENSIONS ARE IN INCHES
TOLERANCES: 0.005

DEBUR AND
BREAK SHARP
EDGES
Carleton University SRCL

NAME | SIGNATURE | DATE | | | | TITLE: DECK (AV + SENS)
Q.A | | | | MATERIAL: ALUMINUM 6061 | SSFP-006 DWG NO. | A3

DRAWN | Justin Kernot | | 06/05/16
CHK'D
APPV'D
MFG

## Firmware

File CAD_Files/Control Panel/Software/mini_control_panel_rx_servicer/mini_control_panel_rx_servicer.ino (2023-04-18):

// Arduino digital pins
#define good 9
#define bad 8
#define SWITCH_PIN  6
#define kill_signal 13
#define restore_signal 20
#define bat_status A2
#define bat_light 7

int last;
int timer;
float time_out = 5; // time out [seconds] how long to wait if no signal is received before freaking out
int start = 0;
int bat;
const int pulse_time = 5000;// how many milliseconds to pulse red LED when no signal is received. should equal time_out
const int low_batt_value = 480;// 23.8 V on the battery
const int critical_battery = 471; // corresponds to 23.3 V on battery (MUST CHARGE BATTERY)

void setup()
{
  pinMode(bat_light, OUTPUT); // low battery LED
  pinMode(good, OUTPUT); // led for good e-stop status
  pinMode(bad, OUTPUT); //led for bad e-stop status
  pinMode(SWITCH_PIN, OUTPUT); // pin that MOSFET is connected to
  digitalWrite(SWITCH_PIN, LOW); // Initializing power to be off until "ready" signal is received from ground station
  digitalWrite(bad, HIGH); // initializing bad LED to be on
  digitalWrite(good, LOW); // turning off good e-stop LED
  digitalWrite(bat_light, LOW); // low battery light off
  Serial.begin(1200);  // Hardware supports up to 2400, but 1200 gives longer range
  delay(250);
}

void loop() // looping forever
{

  if (analogRead(bat_status) < low_batt_value) // if battery is low
  {
    digitalWrite(bat_light, HIGH); // illuminate low battery LED
  }
  if (analogRead(bat_status) < critical_battery) // if battery is critically low
  {
    digitalWrite(SWITCH_PIN, LOW); // kill power
    digitalWrite(good, LOW); // signal e-stop is triggered
    digitalWrite(bad, HIGH);

    while (true) // looping forever until battery gets charged
    {
      digitalWrite(bat_light, HIGH);
      delay(250);
      digitalWrite(bat_light, LOW);
      delay(250);
    }
  }

  int signal = readUInt(true); // read signal from receiver chip

  if (signal == kill_signal || signal == 0 ) // Check to see if we got the e-stop signal or no signal at all
  {
    digitalWrite(SWITCH_PIN, LOW); // if we got the E-STOP signal (13), kill power!!!
    digitalWrite(good, LOW);
    digitalWrite(bad, HIGH); // alert the operator

    while (signal != restore_signal) // while waiting for restore signal
    {
      if (analogRead(bat_status) < low_batt_value) // check if battery is low
      {
        digitalWrite(bat_light, HIGH); // write it as low if low
      }
      if (analogRead(bat_status) < critical_battery) // if battery is critically low
      {
        digitalWrite(SWITCH_PIN, LOW); // kill power
        digitalWrite(good, LOW); // signal e-stop is triggered
        digitalWrite(bad, HIGH);

        while (true) // looping forever until battery gets charged
        {
          digitalWrite(bat_light, HIGH);
          delay(250);
          digitalWrite(bat_light, LOW);
          delay(250);
        }

      }

      if (signal == 0) // if we got no signal, pulse the BAD LED
      {
        digitalWrite(bad, LOW);
        delay(pulse_time);
        digitalWrite(bad, HIGH);
      }
      signal = readUInt(true); // takes up to 5 seconds to execute if no signal comes in

    }// Keep power killed until "RESTORE" signal is received (20)

  }
  digitalWrite(SWITCH_PIN, HIGH); // Since RESTORE signal was received, allow power to flow again
  digitalWrite(good, HIGH);
  digitalWrite(bad, LOW);
}


// Receives an unsigned int over the RF network (not written by Kirk)
unsigned int readUInt(bool wait)
{

#define NETWORK_SIG_SIZE 3
#define VAL_SIZE         2
#define CHECKSUM_SIZE    1
#define PACKET_SIZE      (NETWORK_SIG_SIZE + VAL_SIZE + CHECKSUM_SIZE)

  // The network address byte and can be change if you want to run different devices in proximity to each other without interfearance
#define NET_ADDR 5

  const byte g_network_sig[NETWORK_SIG_SIZE] = {0x8F, 0xAA, NET_ADDR};  // Few bytes used to initiate a transfer

  int pos = 0;          // Position in the network signature
  unsigned int val;     // Value of the unsigned int
  byte c = 0;           // Current byte

  if ((Serial.available() < PACKET_SIZE) && (wait == false))
  {
    return 0;
  }
  unsigned long start = millis();
  while (pos < NETWORK_SIG_SIZE)
  {
    while (Serial.available() == 0) // Wait until something is avalible
    {
      if (millis() - start > time_out * 1000)
      {
        return 0;
      }
    }
    c = Serial.read();

    if (c == g_network_sig[pos])
    {
      if (pos == NETWORK_SIG_SIZE - 1)
      {
        byte checksum;
        unsigned long start = millis();
        while (Serial.available() < VAL_SIZE + CHECKSUM_SIZE) // Wait until something is avalible
        {
          if (millis() - start > time_out * 1000)
          {
            return 0;
          }
        }
        val      =  Serial.read();
        val      += ((unsigned int)Serial.read()) * 256;
        checksum =  Serial.read();

        if (checksum != ((val / 256) ^ (val & 0xFF)))
        {
          // Checksum failed
          pos = -1;
        }
      }
      ++pos;
    }
    else if (c == g_network_sig[0])
    {
      pos = 1;
    }
    else
    {
      pos = 0;
      if (!wait)
      {
        return 0;
      }
    }
    if (millis() - start > time_out * 1000) // if we keep getting errorous data for more than the timeout
    {
      return 0;
    }
  }
  return val;
}

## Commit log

2021-09-09 Transfer v3.07e
    Transfer of SPOT v3.07e from Alex's repository to the official SRCL repository.
    [2-56_flatscrew_91253A078.SLDPRT, 2-56_flatscrew_91253A079.SLDPRT, 2-56_nut_90480A003.SLDPRT, 2-56_socketscrew_91251A079.SLDPRT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]
2021-09-22 updated Estimate_COG with Kirk's newest Red and Black measurements as of July 2021. Red mass properties can be commented/uncommented to be more accurate in different configurations: with/without red 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
2022-02-02 added reaction wheel files
    [Design Calculations.xlsx, Maxon Gearbox.SLDPRT, Maxon Motor.SLDPRT, RWA.SLDASM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]
2022-02-03 adding emergency stop arduino mini code
2022-06-15 SPOT v3.0.8-beta.1 Minor Update-2
    - Added sample code in the Template_Files/Saved Figures/ directory to show how to time align the three packets (one per platform) and convert it to a data class. This makes analysis much easier.
2022-06-16 Uploading obstacle arduino code
2022-12-08 SRCL PowerPoint template files circa May 2022
2023-07-09 SPOT 4.0.0 Beta.1 (RC)
    This marks the release of SPOT 4.0.0 as a release candidate.
    [biases_layer_0.csv, biases_layer_1.csv, weights_layer_0.csv, weights_layer_1.csv]
2023-08-05 SPOT 4.0.0-RC.2
    - Updated the arm simulation code to allow for different friction coefficients at each joint.
    - Removed unused code from the arm simulation section.
    - Fixed a small typo in a tooltip for the main GUI.
    - Added in a UDP send block in the template Simulink file to send data to the NVIDIA Jetson TX2 board. See Wiki entry for details.
    - Created a python script called 'receive_data.py' which can be deployed on the Jetson TX2 to receive data.
    - Added some QOL touches and backend bug fixes.
    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
2023-09-05 SPOT 4.0.0-RC.3
    - Modifed the data inspector load data function so that the GUI returns to the focus of the desktop when the user either cancels or loads data.
    - [Courtesy of Kirk Hovell] Found a longstanding bug that likely resulted in about 2% more air beign used on average. The issues were:
    -- [Red only] The centre of mass offset due to the robot arm is no longer considered when no robot arm is present
    -- [All platforms] The thruster decay due to pressure drop is considered when recalculating the actual achieved thrust (Fx_Sat, Fy_Sat, Tz_Sat). This was done by replacing one of the MakeH blocks wit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
    - Found an error in the GUI in the FireBLUEThrusters callback. The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
2023-09-08 SPOT 4.0.0-RC.4
    - Fixed the ArmConfig.png image so that the body axis orientation is correct.
    - Fixed a bug where if the user saves a GUI state with a diagram selected, when loading the GUI state it will load the diagram (this can lead to problems if you load the state and the diagram is miss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
    - Flip-flopped back to software PWM for the following reasons:
    -- Hardware PWM is best for high frequency problems, where the the pulses are extremely fast. Because of the valve time on the thrusters, is does not make sense to have a high frequency PWM.
    -- The minimum hardware PWM achievable on the PCA9685 is 24 Hz. This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
2024-02-02 SPOT 4.0.0-RC.4 Hotfix #1
    - Updated the PhaseSpace_Server code to use the new LED drivers.
    - Replaced the StreamData executable in the templates folder.
